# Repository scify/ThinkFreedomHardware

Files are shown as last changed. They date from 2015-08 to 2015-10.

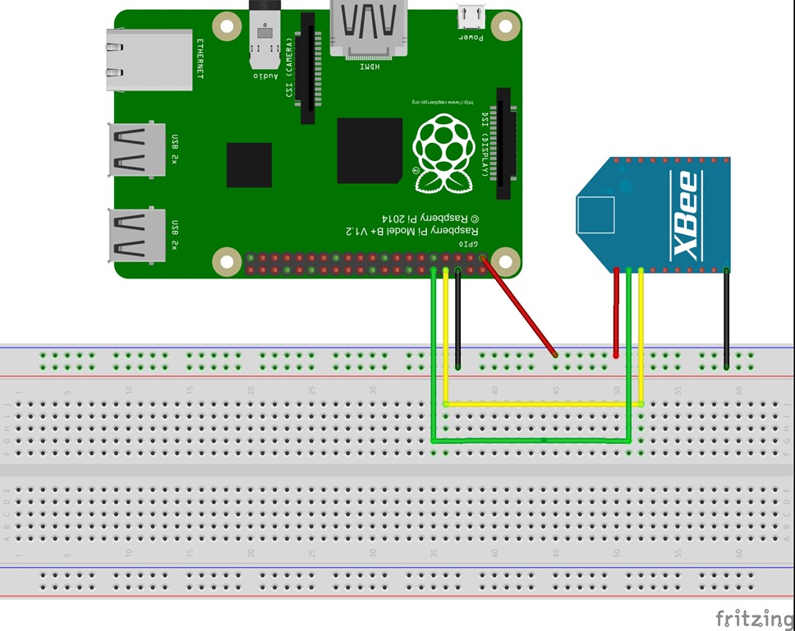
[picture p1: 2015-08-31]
Stuff/Pictures-Schematics/xbee on pi shematic.jpg

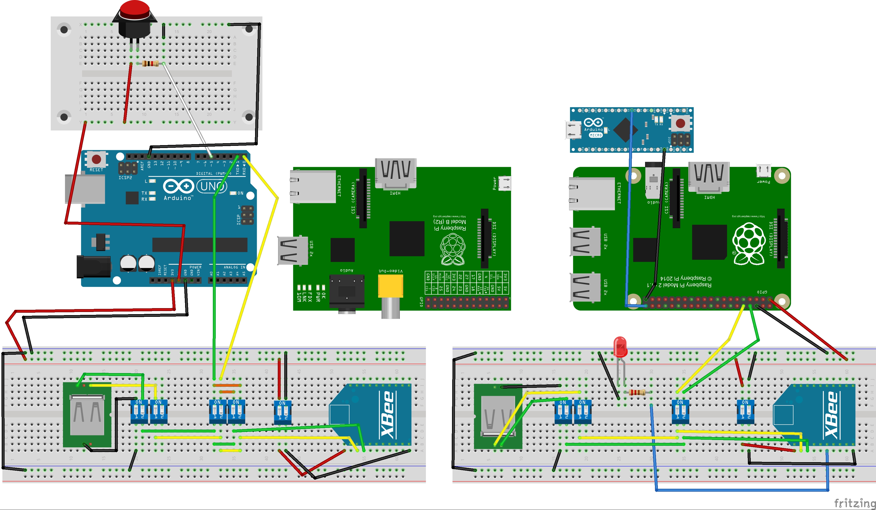
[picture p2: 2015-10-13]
Scematics(Fritzing)/ThinkFreedomStack Schematic(Fritzing)_bb.jpg

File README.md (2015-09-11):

# ThinkFreedom Hardware Stack

The ThinkFreedom Hardware Stack is a hardware stack definition aimed to provide
an open implementation architecture under a
*sensor-stimulus-reactor* paradigm, supporting different settings of the
Internet of Things (IoT).

This specific project refers to the first draft of the hardware stack
definition and a first implementation, as a
device which is especially designed for disabled people. The goal of this
project is to help this group of people to interact with devices in their home
and use the PC and to better communicate with other people.

In this repository you will find a hardware prototype that was built during an
internship at SciFY (www.scify.org). This project is an openhardware-opensource
project.

## Box
Contains 2 versions (v1 and v2) of a 3D design model of the controller . You
can open them with the open source FreeCad program. It contains also a folder
with failed attempts and some examples.

## Code
Contains 3 code "packages".

1. ControlUnitPython.py  this python script runs on the Raspberrry Pi 2
2. TFS_Leonardo.ino this arduino script runs on the Arduino Leonardo/Micro
located in the control unit .
3. TFS_input.ino this arduino script runs on the Arduino Uno located in the
controller

Both arduino scripts can be edited and uploaded with the Arduino program. For
more information on how to use the code snippets check the "Manual of
Prototype" document.

## Schematics(Fritzing)
Contains 2 files.

1. ThinkFreedom Stack.jpg  this is a simple image of the schematic of the
prototype
2. TFS_Leonardo.ino this is a fritzing file which can be edited by the Fritzing
program : http://fritzing.org/home/

## Stuff

Contains several things that helped as along the way.

1. Pictures-Schematics: this file has several schematics images that we
considered when we were making the prototype
2. Alternate Input Ways.docx:  this doc has helpful descriptions of assistive
technology products
3. Switches for Think Freedom.xlsx this ecxel file is one of our first research
of switches that could be used for our application.

## ThinkFreedomStack Specs

Contains the specs for the project as well as it contains the architecture (
1.Layers of TFS(OSI Model).xlsx ) we used to build the prototype. The last file
has 3 additional implementations of the hardware stack and approximations of
costs.

## Manual For Prototype
A step by step guide of how you are going to build the prototype that we
developed.

## TFS_Presentation
Is a presentation of our work on Prezi.

## License

[](http://
creativecommons.org/licenses/by/4.0/)
ThinkFreedom Hardware by [SciFY](http://www.scify.org) is licensed under
a [Creative Commons Attribution 4.0 International
License](http://creativecommons.org/licenses/by/4.0/).
Based on a work at
[https://github.com/scify/ThinkFreedomHardware](https://github.com/scify/
ThinkFreedomHardware).

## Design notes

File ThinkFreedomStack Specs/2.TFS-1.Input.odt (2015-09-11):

TFS 1. Input

The input in general should changeable, it depends on the person that is going to use the device . For different type of inputs it should give the same signal to the control unit(for example the input can be buttons ,a joystick , a camera or it can be sensors). Keeping that in mind for selecting the input. It can be:

Buttons/Switches:

-It can be a Button. This requires the help from the software. For example a keyboard, there has to be a way of moving from key to key and the button should be the selection.

-It can be a combination of Buttons. This way more complex things can be operated by the user. The help from for the software is much less needed.

There are a lot types of buttons/switches that can be used. Link:

https://docs.google.com/spreadsheets/d/1ZvIIkGd06QHr9OYzwCT2-BUQOSj6Ud6AHfjPr6JeUGU/edit?usp=sharing

Sensors:

The type of sensors that can be used are:

-Optical. It can be a camera that can detect movement. It can be eye movement, face gestures, head movement or body movement.

-Tilt. The user can just move his head to operate the system.

An interesting idea is this : https://www.youtube.com/watch?v=ikD_3Vemkf0

Joystick:

Instead of a mouse(or something else with the help of the software) the user will use a joystick. It can be combined with buttons for clicking or selecting.

Some other input ways can be found here:

https://docs.google.com/document/d/1bNMofBS1oewYr8HfNjX6Wp-dU_9WeOqa6330RUK6RvI/edit?usp=sharing

Specs about the way the signal is going through the channel.

The trigger from the input must be altered so it can much the channel that is going to be transmitted to the control unit. That means it must support the way the control unit receives the signals ( for example via bluetooth, cable, internet).

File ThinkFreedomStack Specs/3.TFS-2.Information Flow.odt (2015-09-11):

TFS-2.Information Flow

Αυτό το επίπεδο περιλαμβάνει τη μεταφορά της πληροφορίας του φυσικού ερεθίσματος στην μονάδα επεξεργασίας στην σωστή μορφή . Αναλύοντας αυτό το επίπεδο ξεχωρίζουμε χονδρικά : κωδικοποίηση της ερεθίσματος , μεταφορά του μέσω καναλιού , αποκωδικοποίηση και εισαγωγή του στην μονάδα επεξεργασίας .

Οι πιο πρακτικοί τρόποι υλοποίησης αυτού το επίπεδου για αυτό το project είναι με καλώδιο (USB) , ZigBee, bluetooth , υπέρυθρες και ίσως Wi-fi ή GSM .

Για τα παραπάνω υπάρχουν πολλές διαφορετικές επιλογές στο εμπόριο όπως :

http://gr.mouser.com/Embedded-Solutions/RF-Wireless-Modules/Bluetooth-802151-Modules/_/N-6l7pgZscv7Zlls6

https://www.microchip.com/pagehandler/en-us/technology/bluetooth/home.html

http://www.zigbee.org/

...για περισσότερα Wi-fi ανατρέξτε στο αρχείο Layer 2-Inputs and Outputs σελίδα 7

Όμως, επειδή για τέτοιες εφαρμογές υπάρχει πολύ υλικό και υποστήριξη στο internet χρησιμοποιώντας το arduino και το raspberry pi κτλ , είναι μια πολύ καλή και φτηνή λύση με μεγάλη συμβατότητα στους διαφορετικούς τρόπους σύζευξης συσκευών με αυτά .

Άρα ,

Κωδικοποίηση ερεθίσματος

-Κάποιο arduino μικρής κατανάλωσης και μεγέθους .

https://www.arduino.cc/en/Main/Products

-Intel Edison (μικρή κατανάλωση και μέγεθος , συμβατότητά , Linux , )

http://download.intel.com/support/edison/sb/edison_pb_331179001.pdf

-Intel Galileo (συμβατό με Αrduino Uno Shields , ethernet )

http://www.intel.com/newsroom/kits/quark/galileo/pdfs/Intel_Galileo_Datasheet.pdf

Μεταφορά μέσω καναλιού + αποκωδικοποίηση και εισαγωγή του στην μονάδα επεξεργασίας

(USB)

-Απλή σύνδεση του arduino με μακρύ καλώδιο USB (ή micro-USB) και στις δυο άκρες

(Bluetooth)

- Χρήση κατάλληλου bluetooth chip για το οποίο υπάρχουν έτοιμες βιβλιοθήκες για arduino

http://www.ebay.com/bhp/arduino-bluetooth

https://store.arduino.cc/index.php?main_page=advanced_search_result&search_in_description=1&keyword=bluetooth&btnG=search

(Υπέρυθρες)

-Αντίστοιχο με το προηγούμενο

http://www.ebay.com/bhp/arduino-ir-sensor

(Wifi)

-Ένα Wi-fi Shield μπορεί να παρέχει μη τοπική επεξεργασία της πληροφορίας με δυνατότητα επικοινωνίας με από σημεία στο χώρο με wifi

http://www.ebay.com/sch/i.html?_from=R40&_trksid=p2053587.m570.l1313.TR0.TRC0.H0.Xwifi+shield+arduino.TRS0&_nkw=wifi+shield+arduino&_sacat=0

(GSM)

-Αντίστοιχο με το προηγούμενο μόνο που εδώ έχουμε επικοινωνία (σχεδόν) σε κάθε χωρικό σημείο

https://www.arduino.cc/en/Main/ArduinoGSMShield

http://www.ebay.com/sch/i.html?_odkw=wifi+shield+arduino&_osacat=0&_from=R40&_trksid=p2045573.m570.l1313.TR0.TRC0.H0.XGSM+shield+arduino.TRS0&_nkw=GSM+shield+arduino&_sacat=0

Τώρα , μπορεί να γίνει και συνδυασμός των παραπάνω για μια πιο ολοκληρωμένη λύση . Για παράδειγμα , όταν υπάρχει ταυτόχρονα bluetooth και wifi (ή GSM) και η σύνδεση μέσω του πρώτου διακοπεί ,τότε μπορεί να αναλάβει το δεύτερο ενεργοποιώντας διαφορετικές δυνατότητες του λογισμικού . Πιο συγκεκριμένα , επειδή η διακοπή της σύνδεσής με bluetooth σημαίνει οτι , είτε ότι το άτομο απομακρύνθηκε από το χώρο , είτε μια διακοπή του ρεύματος , είτε γενικότερη αποτυχία στην σύνδεση , τότε το wifi και το GSM θα παρέχει μια μεγαλύτερή κάλυψη ώστε σε περίπτωση ανάγκης να αποστέλνεται ένα email ή sms.

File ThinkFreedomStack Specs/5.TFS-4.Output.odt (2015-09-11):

TFS-4.Output

In general we want the output device to be pretty much everything (TV, smart TV, PC, tablet). After the Control Unit we want the signal to be sent to an adaptor. The adaptor will alter the signal so it will match the output devices in each case.

The communication between the Control Unit and the adaptor it’s going to be materialized in many ways so the Think Freedom device is going to be more easy to use and more accessible for everyone. The communication ways are via Internet(wifi and ethernet), cable, bluetooth.

TV

If the Think Freedom device is going to be connected to a TV(via VGA or HDMI) the Control Unit should be able to support an OS or a specific software.

Smart TV

Here the software can be installed in the smart TV so the Control Unit should only give the signal to trigger some functions in the software. Also the Smart TV can be connected to internet, for distant control.

PC

If the output device is a PC the Think Freedom device should work like an input device for the PC, like a mouse or a keyboard. The laptop must have the software of Think Freedom installed.

Tablet

For the Think Freedom device to work on a tablet there has to be an app for the tablet. The device can be connected via bluetooth or internet with the tablet.

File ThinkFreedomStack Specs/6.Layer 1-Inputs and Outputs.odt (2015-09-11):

Layer 1-Inputs and Outputs

Inputs

-Buttons/switch

This type of input is a signal(pulse). Τhe signal can be 1V-5V.

This applies to the buttons/switches with a mono phone plug output. The tip send the signal and the sleeve is the ground. The circuit is shown below:

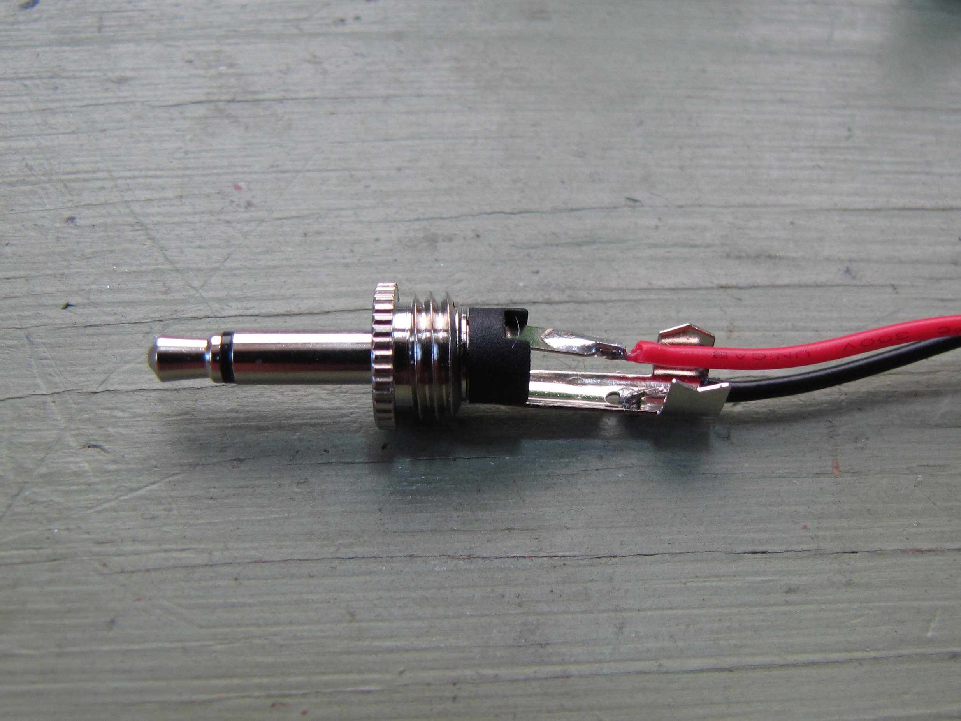
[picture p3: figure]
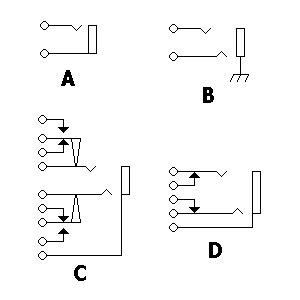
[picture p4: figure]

Left the mono phone plug. Right the A the input.

- joystick

The types of joysticks a many. The most common one is the type that works like a combination of buttons.

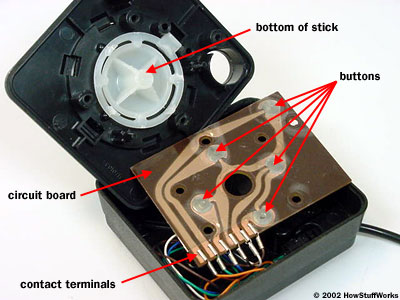
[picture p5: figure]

The button type switch circuit

The output of this is either a usb device or some kind of connector.

-Camera

If a camera is going to be the input, we need some process in this level. Also we need the help of the software in a next level. Also that means that the input layer must have a driver to support a camera.

-Sensors

The type of signal we are going to have depends on the sensor we are going to use. In general is pretty easy to handle the signal of a sensor with a microcontroller.

The signal from from the sensor depends on the type of sensor we are going to use. In general it is from some mVs to some Volts. This signal must be processed

Some sensors are:

pressure sensor

A pressure sensor is generally a variable resistor that changes resistance based on how hard it is pressed. They are also known as Force Sensing Resistors or FSRs. They come in many shapes and sizes, from tiny little dots to long strips. They're pretty flexible, and can usually be cut to size.

Often you use an FSR as the variable resistor in a voltage divider circuit. By using one FSR and one fixed resistor and hooking Vout to an A/D converter you can give the microcontroller some idea of how much pressure is being put on the FSR. If you don't have an A/D converter handy, there's a simple RCtime circuit that you can use to do more-or-less the same thing.

FSRs can be used in many places that a button is used, with the advantage that you can not only tell that the button is being pressed, but also how hard. They're used a lot in things like velocity-sensitive keyboards, but are also good for use in floor mats, on the sides of instruments, on finger tips...Basically anywhere there's going to be a force that you want to measure.

light sensor

The most common light sensor is the CDC photo sensor. It works like a variable resistor with a value that changes based on how much light it receives. Other types are photo-transistors and photo-diodes.

Photo sensors are used in much the same way as pressure sensors. If you hook one up to a microcontroller via a voltage divider (or RCtime) circuit, the microcontroller can sense how much light is falling on the device.

beam breaker

A beam breaker is a non-physical switch or trigger. The simplest way to make one is to aim a cheap laser pointer at a photo-sensor. When the beam is broken, the resistance of the photo-resistor changes. If the photo resistor is hooked up to a microcontroller, it can sense whether the beam is intact or broken. So simple!

proximity sensor

There are a variety of ways to implement proximity sensing. The most common are infrared and ultrasound. They're both usually used as packaged devices that hook up to a microcontroller via one or more digital i/o lines.

An infrared sensor works by sending out pulses of infrared (invisible) light. It then tries to detect reflections of that light from nearby objects. If it detects a reflection then it assumes that there's an object nearby and puts out a digital "1". Otherwise it puts out a "0". There are some tricks to get a rough distance measurement out of an infrared detector, but most often they're used for simple object detection.

An ultrasonic proximity detector works by putting out ultrasonic (inaudible) pulses of sound. It then measures the length of time it takes those pulses to hit nearby objects and return as echos. The longer the time, the farther away the object. Ultrasonic proximity detectors are good for measuring short distances (maybe a couple yards). It's usually up to the microcontroller to do the counting and distance computations; the detector takes care of sending and detecting the ultrasonic pulses.

accelerometer

Accelerometers are cool. They're small ICs with tiny little suspended weights embedded in them. By measuring the force of gravity/inertia on those weights the device can emit a digital signal that tells you about its orientation in space.

Like proximity sensors, accelerometers are hooked up to a microcontroller via a few digital i/o lines.

microphone

Most microcontrollers aren't fast enough to be useful for recording sound via a mic. But they can do some basic things like listen for suddens sounds or listen for silence. They can also be used to control sound recording devices.

contact mic

These are made from piezo elements. A piezo element is made from a curious type of ceramic material that gives off electricity when it's deformed (this is called the piezo-electric effect). The voltage created is (roughly) proportional to how much the element is deformed. This property lets it be used as a contact mic. You can scream all you want into a contact mic and it won't hear you. But rub it against something, and it will wail! There are other types of piezo materials, like piezo rubber.

Output

-cable

usb 2.0

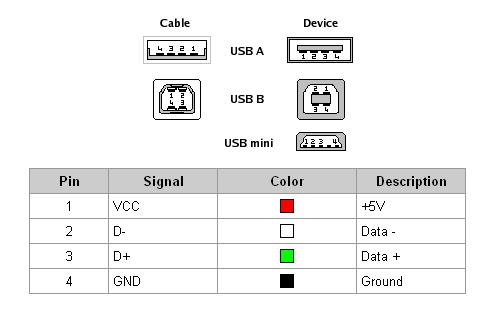
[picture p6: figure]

As we can see there are four pins for the usb . Two pins VCC 5v,Ground and two pins for the data (D+,D-).

Max signaling rate 480Mbit/s.

usb 3.0

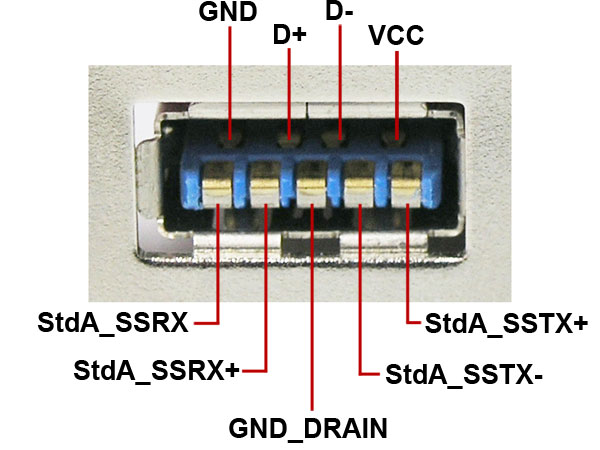
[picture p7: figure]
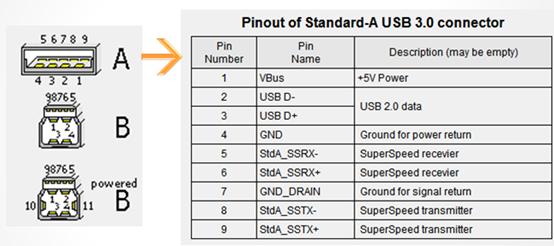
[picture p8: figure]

Throughput 4Gbits/sec.

In conclusion using a usb cable we need a signal in (pulse) and 5V power supply.

-Bluetooth

Bluetooth is a wireless technology standard for exchanging data over short distances (using short-wavelength UHF radio waves in the ISM band from 2.4 to 2.485 GHz] (https://en.wikipedia.org/wiki/Bluetooth#cite_note-4)) from fixed and mobile devices, and building personal area networks (PANs).

Bluetooth operates at frequencies between 2400 and 2483.5 MHz (including guard bands of 2 MHz at the bottom end and 3.5 MHz at the top).This is in the globally unlicensed (but not unregulated) Industrial, Scientific and Medical (ISM) 2.4 GHz short-range radio frequency band. Bluetooth uses a radio technology called frequency-hopping spread spectrum. Bluetooth divides transmitted data into packets, and transmits each packet on one of 79 designated Bluetooth channels. Each channel has a bandwidth of 1 MHz. Bluetooth 4.0 uses 2 MHz spacing, which accommodates 40 channels. The first channel starts at 2402 MHz and continues up to 2480 MHz in 1 MHz steps. It usually performs 1600 hops per second, with Adaptive Frequency-Hopping (AFH) enabled.

Originally, Gaussian frequency-shift keying (GFSK) modulation was the only modulation scheme available. Since the introduction of Bluetooth 2.0+EDR, π/4-DQPSK (Differential Quadrature Phase Shift Keying) and 8DPSK modulation may also be used between compatible devices. Devices functioning with GFSK are said to be operating in basic rate (BR) mode where an instantaneous data rate of 1 Mbit/s is possible. The term Enhanced Data Rate (EDR) is used to describe π/4-DPSK and 8DPSK schemes, each giving 2 and 3 Mbit/s respectively. The combination of these (BR and EDR) modes in Bluetooth radio technology is classified as a "BR/EDR radio".

Bluetooth is a packet-based protocol with a master-slave structure. One master may communicate with up to seven slaves in a piconet. All devices share the master's clock. Packet exchange is based on the basic clock, defined by the master, which ticks at 312.5 µs intervals. Two clock ticks make up a slot of 625 µs, and two slots make up a slot pair of 1250 µs. In the simple case of single-slot packets the master transmits in even slots and receives in odd slots. The slave, conversely, receives in even slots and transmits in odd slots. Packets may be 1, 3 or 5 slots long, but in all cases the master's transmission begins in even slots and the slave's in odd slots.

The above is valid for "classic" BT. Bluetooth Low Energy, introduced in the 4.0 specification, uses the same spectrum but somewhat differently

Officially Class 3 radios have a range of up to 1 metre (3 ft), Class 2, most commonly found in mobile devices, 10 metres (33 ft), and Class 1, primarily for industrial use cases,100 metres (300 ft). Bluetooth Marketing qualifies that Class 1 range is in most cases 20–30 metres (66–98 ft), and Class 2 range 5–10 metres (16–33 ft).

Table of power and range per class

Class | Max permitted power (mW) | Max permitted power (dB) | Range (m)
1 | 100 | 20 | 100
2 | 2.5 | 4 | 10
3 | 1 | 0 | 1

Table of data rate and throughput per Version

Version | Data rate | Max application throughput
1.2 | 1 Mbit/s | >80 kbit/s
2.0+EDR | 3 Mbit/s | >80 kbit/s
3.0+HS | 24 Mbit/s | See (https://en.wikipedia.org/wiki/Bluetooth#Bluetooth_v3.0_.2B_HS)Version 3.0 + HS (https://en.wikipedia.org/wiki/Bluetooth#Bluetooth_v3.0_.2B_HS)
4.0 | 24 Mbit/s | See (https://en.wikipedia.org/wiki/Bluetooth#Bluetooth_v4.0)Version 4.0 LE (https://en.wikipedia.org/wiki/Bluetooth#Bluetooth_v4.0)

- ZigBee

ZigBee is poised to become the global control/sensor network standard. It has been designed to provide the following features:

- Low power consumption, simply implemented
  - Users expect batteries to last many months to years! Consider that a typical single family house has about 6 smoke/CO detectors. If the batteries for each one only lasted six months, the home owner would be replacing batteries every month!
- In contrast to Bluetooth, which has many different modes and states depending upon your latency and power requirements, ZigBee/IEEE 802.15.4 has two major states: active (transmit/receive) or sleep. The application software needs to focus on the application, not on which power mode is optimum for each aspect of operation.
- Even mains powered equipment needs to be conscious of energy. ZigBee devices will be more ecological than their predecessors saving megawatts at it full deployment. Consider a future home that has 100 wireless control/sensor devices,
  - Case 1: 802.11 Rx power is 667 mW (always on)@ 100 devices/home & 50,000 homes/city = 3.33 megawatts
  - Case 2: 802.15.4 Rx power is 30 mW (always on)@ 100 devices/home & 50,000 homes/city = 150 kilowatts
  - Case 3: 802.15.4 power cycled at .1% (typical duty cycle) = 150 watts
- Low cost to the users means low device cost, low installation cost and low maintenance.
  - ZigBee devices allow batteries to last up to years using primary cells (low cost) without any chargers (low cost and easy installation). ZigBee's simplicity allows for inherent configuration and redundancy of network devices provides low maintenance.
- High density of nodes per network
  - ZigBee's use of the IEEE 802.15.4 PHY and MAC allows networks to handle any number of devices. This attribute is critical for massive sensor arrays and control networks.
- Simple protocol, global implementation
  - ZigBee's protocol code stack is estimated to be about 1/4th of Bluetooth's or 802.11's. Simplicity is essential to cost, interoperability, and maintenance. The IEEE 802.15.4 PHY adopted by ZigBee has been designed for the 868 MHz band in Europe, the 915 MHz band in N America, Australia, etc; and the 2.4 GHz band is now recognized to be a global band accepted in almost all countries.

ZigBee/IEEE 802.15.4 - General Characteristics

- Dual PHY (2.4GHz and 868/915 MHz)
  - Data rates of 250 kbps (@2.4 GHz), 40 kbps (@ 915 MHz), and 20 kbps (@868 MHz)
  - Optimized for low duty-cycle applications (<0.1%)
  - CSMA-CA channel access
  - - Yields high throughput and low latency for low duty cycle devices like sensors and controls
  - Low power (battery life multi-month to years)
  - Multiple topologies: star, peer-to-peer, mesh
  - Addressing space of up to:
  - - 18,450,000,000,000,000,000 devices (64 bit IEEE address)
  - - 65,535 networks
  - Optional guaranteed time slot for applications requiring low latency
  - Fully hand-shaked protocol for transfer reliability
  - Range: 50m typical (5-500m based on environment)

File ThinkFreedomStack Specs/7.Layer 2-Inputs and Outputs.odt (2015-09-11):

Layer 2 - Inputs and Outputs

Περιγραφή Απαιτήσεων

*Τα κείμενα σε γκρι χρώμα είναι επιβοηθητικά.

Η επικοινωνία ανάμεσα στη μονάδα επεξεργασίας και και το σύστημα που υλοποιεί το ερέθισμα θα πρέπει να έχουν αμερόληπτη επικοινωνία μεταξύ τους . Παρόλα αυτά οι απαιτήσεις του έργου δεν είναι υψηλές και επομένως μπορούν να προσδιοριστούν κάποιες απλές προδιαγραφές :

Για ενσύρματη επικοινωνία

Θα πρέπει να επιτυγχάνεται μια μετάδοση παλμός σε ακολουθία , η οποία θα διαμορφώνεται από το προηγούμενο layer στου οποίου θα είναι η έξοδος

Δεν έχουμε απαίτηση μεγάλου μήκους καλωδίου , οπότε δεν μας απασχολεί η ποιότητα του καλωδίου διότι η εξασθένηση και η διασπορά των παλμών θα είναι αμελητέες.

Η τάση λειτουργίας είναι ένα από τα μελήματα μας καθώς σε dc δεν πρέπει να ξεπερνιούνται τα 100 V . Η εφαρμογή μας όμως είναι τέτοιας κλίμακας που δεν μας απασχολεί κάτι τέτοιο .

Ενδεικτικά το άνω όριο της ίασης που θα χρησιμοποιήσουμε είναι στα 5V .

Ας έχουμε στο μυαλό μας πως το καλώδιο θα πρέπει να είναι καλά ενισχυμένο και μονωμένο . Οι ασθενείς που θα το χρησιμοποιήσουν δεν είναι σε θέση να πραγματοποιήσουν ακριβής κινήσεις ώστε να προσέξουν τις προκαλούμενες καταπονήσεις που μπορεί να προκαλέσουν στο καλώδιο . Αντοχή στον εφελκυσμό , αντοχή στον τεμαχισμό, αντοχή στις υψηλές θερμοκρασίες , υψηλή μόνωση πρέπει να εξασφαλιστούν ώστε να μην διακοπεί πότε η επικοινωνία .

Φυσικά και οι δυο άκρες πρέπει να μιλούν την ίδια `γλώσσα` . Αυτό σημαίνει πως πρέπει να υπάρχει ένα ενιαίο πρωτόκολλο επικοινωνίας . Αυτό θα πρέπει να καθορίζει το τι θα στέλνει η συσκευή ώστε ο παραλήπτης , η μονάδα επεξεργασίας , να το καταλαβαίνει . Δηλαδή και οι δυο άκρες πρέπει να μετασχηματίζουν το μήνυμα σύμφωνα με ένα κανόνα που θα έχουν από κοινού , ακόμα και αν τρέχουν διαφορετικά λειτουργικά συστήματα . Υπάρχουν ήδη πολλές αναπτυσσόμενες τεχνολογίες που προσφέρουν μεγάλη συμβατότητα και εμείς θα επιλέξουμε μια ευρέος διαδεδομένη .

Για ασύρματη επικοινωνία

Πάλι εδώ πρέπει να αποστείλουμε ένα μήνυμα αποτελούμενο από μια ακολουθία παλμών (ψηφιακή μετάδοση ) αλλά αυτήν την φορά ασύρματα , δηλαδή ακολουθία ηλεκτρομαγνητικών παλμών οι οποίοι παράγονται από την έξοδο του προηγουμένου από αυτού layer .

(

Considerations in choosing a carrier frequency

Carrier frequency

Signal that is modulated to carry data

Frequency is not equal to bandwidth

Ability to carry data (modulation rate)

Availability of devices to transmit and receive signals

Interference from other devices in same band *

ISM bands limit power output

Interactions of radiation with environment absorption by water, metal, building materials, foliage

Reflection and multi-path properties constructive/destructive interference patterns (e.g., nulls)

)

Ο ρυθμός μετάδοσης των bit δεν έχει πολύ σημασία αφού τεχνολογίες υπερκαλύπτουν της απαιτήσεις του έργου

Δεν έχουμε απαίτηση μεγάλης απόστασης μετάδοσης αφού η ασύρματη σύνδεση που θέλουμε να πραγματοποιήσουμε είναι σε μικρή απόσταση ( ~ 10m ) και επιθυμούμε μια απλή και άμεση επικοινωνία δυο συσκευών . Επομένως δεν χρειάζεται να στηθεί κάποιο κεντρικό σημείο πρόσβασης . Αντιπροσωπευτικός τύπος μιας τέτοιες σύνδεσης είναι το ad hoc (point-to-point) τύπος δικτύου (βλ. Bluetooth κτλ) . Προσφέροντας έτσι ευελιξία , ελάχιστη διαμόρφωση , γρήγορη εγκατάσταση (και αλλά) στον τρόπο σύνδεσης ανάμεσα στις συσκευές , αυτό δεν σημαίνει παράλληλα πως ένα access point (Star pattern) δίκτυο δεν είναι κατάλληλο (βλ Wifi , Cellular κτλ ) .

Μας απασχολεί το εύρος συχνοτήτων που θα καταλαμβάνει ώστε να μην έχουμε παρεμβολές . Οι διαθέσιμες συχνότητες για την εφαρμογή μας είναι από τα 300 MHz έως τα 30 GHz περίπου . Μερικές από αυτές τις συχνότητες μέσα σε αυτό το εύρος είναι αξιοποιήσιμες για την εφαρμογή μας , διότι πολλές είναι , και πάλι , δεσμευμένες για άλλες χρήσεις . Ως γνωστόν διαφορετικές συχνότητες προσδίδουν διαφορετικά χαρακτηριστικά ανάκλασης , διάθλασης , περίθλασης άλλα εδώ δεν μας απασχολούν πολύ αυτά γιατί δεν έχουμε μεγάλες αποστάσεις ούτε και σημαντικά εμπόδια .Επίσης προτείνεται η διαίρεση στο χρόνο πολύπλεξη (TDM) για την αμφίδρομη επικοινωνία διότι είναι πιο αξιόπιστη. Σε περιπτώσεις που το εύρος που επιλέγει υπερκαλύπτει μερικώς ή τελείως υπηρεσίες με αντίστοιχα εύρη , τότε να ληφθούν υπόψη οι τεχνικές FDSS και DSSS.

Προτεινόμενες τεχνολογίες είναι Bluetooth (2,4-2,485GHz) , WiFi/802.11b/g and Bluetooth: 2.4GHz , Cell phones: 824-849MHz, 869-894MHz, 1850-1990MHz , Zigbee/802.15.4: 868MHz, 915MHz, 2.4GHz .

Η κατανάλωση ισχύος πρέπει να είναι μικρή γιατί η συχνή φόρτιση του ασύρματου χειριστηρίου θα δυσχεραίνει την επικοινωνία με την μονάδα επεξεργασίας . Για τον ασθενή δεν είναι αυτονόητο πως θα μπορεί εύκολα να φορτίζει το χειριστήριο συχνά και επίσης δεν πρέπει να κοπεί ξαφνικά η σύνδεση . Άρα , η τεχνολογία που θα επιλέγει πρέπει να είναι χαμηλής κατανάλωσης (βλ. ZigBee , Bluetooth κτλ )

Προς την ίδια κατεύθυνση πρέπει και το πρωτόκολλο επικοινωνίας να επιτρέπει την εύκολη διακοπή της σύνδεσης . Ακόμα και αν η τεχνολογία , που τελικά θα επιλέγει , καθορίσει τα διαθέσιμα πρωτόκολλα που μπορούμε να επιλέξουμε , αυτό δεν σημαίνει πως δεν χρειάζεται να ασχοληθούμε με αυτά . Αν κάποιος διαλέξει να υλοποιήσει μια διαφορετική τεχνολογία , το πρωτόκολλο επικοινωνίας πρέπει να εξασφαλίζει την επιτυχία παράδοσης του μηνύματος στον παραλήπτη με κάθε κόστος και ίσως να εκφράζει ένα ασύρματο προσωπικό δίκτυο (WPAN)

ZigBee καλό http://courses.cs.washington.edu/courses/csep567/10wi/lectures/Lecture8.pdf

(

Radio Protocols for Wireless Networks

UHF (300-1000MHz)

Mote radio

WiFi (2.4GHz)

Wireless LAN Bluetooth (2.4GHz)

Common in many consumer devices (PDAs, cell phones, etc.)

Zigbee (850-930MHz)

Next generation radio for sensor networks and consumer devices

Bluetooth

Short-range radio at 2.4GHz

Available globally for unlicensed users

Low-power Low-cost Cable replacement

Devices within 10m can share up to 1Mb/sec – 700Kb/sec effective

Universal short-range wireless capability

Bluetooth Application Areas

Data and voice access points

Real-time voice and data transmissions

Cordless headsets

Three-in-one phones: cell, cordless, walkie-talkie

Cable replacement

Eliminates need for numerous cable attachments for connection

Automatic synchronization when devices within range

Ad hoc networking

Can establish connections between devices in range

Devices can “imprint” on each other so that authentication is not required for each instance of communication

Support for object exchange (files, calendar entries, business cards)

)

[synexeia apo https://el.wikipedia.org/wiki/%CE%91%CF%83%CF%8D%CF%81%CE%BC%CE%B1%CF%84%CE%BF_%CE%B4%CE%AF%CE%BA%CF%84%CF%85%CE%BF

https://en.wikipedia.org/wiki/Wireless#Wireless_services

https://en.wikipedia.org/wiki/Bluetooth]

Εύρεση υπαρχόντων λύσεων

Σε αυτό το σημείο θα γίνει η αντιστοίχηση των παραπάνω προδιαγραφών κάποιες τεχνολογίες που τις πληρούν σε πολύ καλό βαθμό.

Για ενσύρματη επικοινωνία

USB

Το USB σχεδιαστικέ για να βοηθήσει την σύνδεση διαφόρων συσκευών με τον υπολογιστή με έναν κοινό τρόπο . Επομένως ικανοποιεί πολύ καλά τις προδιαγραφές μας και είναι μια δομημένη και προτιμητέα σύνδεση από πολλές εφαρμογές.

Υπάρχει αναφορά στην περιγραφή του Layer 1.

Δεν χρειάζεται να μπούμε σε λεπτομέρειες υλοποίησης για το συγκεκριμένο έργο γιατί οι περισσότερες ενσύρματες διεπαφές προβλέπουν ένα USB.

Για ασύρματη επικοινωνία

ZigBee

Ας έχουμε υπόψη ότι τόσο το πρότυπο Bluetooth όσο και το ZigBee θεωρούνται ως μια ασύρματη USB σύνδεση.

Ο όρος Zigbee αναφέρεται στο πρότυπο ΙΕΕΕ 802.15.4 το οποίο περιγράφει μια ομάδα πρωτοκόλλων για την επικοινωνία ραδιοσυκευών πολύ μικρού μεγέθους, κόστους και πολύ χαμηλής ισχύος. Το πρότυπο στοχεύει στα ασύρματα προσωπικά δίκτυα και συγκεκριμένα στοχεύει στην αντικατάσταση του Bluetooth καθώς οι ραδιοσυσκευές του πρότυπου Zigbee είναι πιο φτηνές και απαιτούν περίπου το 50% του κώδικα που χρειάζεται μια συσκευή Bluetooth για τον έλεγχο τους (κατά συνέπεια απαιτούν λιγότερο χώρο στη μνήμη της φορητής συσκευής – γεγονός σημαντικό για τις μικρές μνήμες). Το πρότυπο χρησιμοποιεί τις ίδιες συχνότητες με το Bluetooth μπορεί να χρησιμοποιηθεί για ασύρματη επικοινωνία χαμηλών ταχυτήτων όπου η ασφάλεια και η διάρκεια ζωής της μπαταρίας είναι τα βασικά στοιχεία.

Παρατίθενται κάποια βασικά χαρακτηριστικά του που το δικαιολογούν ως μια ικανοποιητική λύση για το έργο.

-Simple protocol (small memory footprint for protocol stack)

-Broadcast support (unlike Bluetooth)

-Full network support (up to 64-bit addresses)

-Very low power (batteries that last years)

-Consumer device networks

-Remote monitoring and control

-Low-cost, low-complexity

-Support ad-hoc and mesh networking

-Industry consortium

-Builds on IEEE standard 802.15.4 physical radio standard – OQSK encoding (offset quadrature phase shift keyed)

-Adds logical network, security and application software 250Kb/sec bandwidth – 128Kb/sec effective, 30m range at 2.4GHz 40Kb/sec at 915MHz

Υπάρχει αναφορά στην περιγραφή του Layer 1.

Τα ακριβής χαρακτηριστικά μερικών μοντέλων βρίσκονται παρακάτω :

https://www.silabs.com/products/wireless/zigbee/Pages/zigbee-chips.aspx

http://www.digi.com/products/wireless-wired-embedded-solutions/zigbee-rf-modules/zigbee-mesh-module/xbee-zigbee#overview

http://www.zigbee.org/zigbee-products-2/#zigbeecertifiedproducts/?view_30_filters=%5B%7B%22field%22%3A%22field_3%22%2C%22operator%22%3A%22is%22%2C%22value%22%3A%22551ed892f6cde90637f85dcb%22%7D%5D&view_30_page=1

Bluetooth

Το Bluetooth είναι ένα βιομηχανικό πρότυπο για ασύρματα προσωπικά δίκτυα υπολογιστών (Wireless Personal Αrea Νetworks, WPAN (https://el.wikipedia.org/wiki/WPAN)). Πρόκειται για μια ασύρματη τηλεπικοινωνιακή (https://el.wikipedia.org/wiki/%CE%A4%CE%B7%CE%BB%CE%B5%CF%80%CE%B9%CE%BA%CE%BF%CE%B9%CE%BD%CF%89%CE%BD%CE%AF%CE%B5%CF%82) τεχνολογία μικρών αποστάσεων, η οποία μπορεί να μεταδώσει σήματα (https://el.wikipedia.org/wiki/%CE%A3%CE%AE%CE%BC%CE%B1_(%CE%B7%CE%BB%CE%B5%CE%BA%CF%84%CF%81%CE%BF%CE%BB%CE%BF%CE%B3%CE%AF%CE%B1)) μέσω μικροκυμάτων (https://el.wikipedia.org/wiki/%CE%9C%CE%B9%CE%BA%CF%81%CE%BF%CE%BA%CF%8D%CE%BC%CE%B1%CF%84%CE%B1) σε ψηφιακές (https://el.wikipedia.org/w/index.php?action=edit&redlink=1) συσκευέ (https://el.wikipedia.org/w/index.php?title=%CE%A3%CF%85%CF%83%CE%BA%CE%B5%CF%85%CE%AE&action=edit&redlink=1)ς .Ας έχουμε υπόψη ότι τόσο το πρότυπο Bluetooth όσο και το ZigBee θεωρούνται ως μια ασύρματη USB σύνδεση. Παρατίθενται κάποια βασικά χαρακτηριστικά του που το δικαιολογούν ως μια ικανοποιητική λύση για το έργο.

Protocol Architecture

Cable replacement protocol

RFCOMM

Telephony control protocol

Telephony control specification – binary (TCS BIN)

Adopted protocols

PPP

TCP/UDP/IP

OBEX

WAP

Profiles – vertical slide through the protocol stack

Basis of interoperability

Each device supports at least one profile

Defined based on usage models e.g., headset, camera, personal server, etc.

Bluetooth

Short-range radio at 2.4GHz

Available globally for unlicensed users

Low-power Low-cost Cable replacement

Devices within 10m can share up to 1Mb/sec – 700Kb/sec effective

Universal short-range wireless capability

Bluetooth Application Areas

Data and voice access points

Real-time voice and data transmissions

Cordless headsets

Three-in-one phones: cell, cordless, walkie-talkie

Cable replacement

Eliminates need for numerous cable attachments for connection

Automatic synchronization when devices within range

Ad hoc networking

Can establish connections between devices in range

Devices can “imprint” on each other so that authentication is not required for each instance of communication

Support for object exchange (files, calendar entries, business cards)

Υπάρχει αναφορά στην περιγραφή του Layer 1.

Τα ακριβής χαρακτηριστικά μερικών μοντέλων βρίσκονται παρακάτω :

http://www.ebay.com/bhp/arduino-bluetooth

https://store.arduino.cc/index.php?main_page=advanced_search_result&search_in_description=1&keyword=bluetooth&btnG=search

http://blog.miguelgrinberg.com/post/a-cheap-bluetooth-serial-port-for-your-raspberry-pi

https://www.adafruit.com/products/1327

``Bluetooth vs. Wi-Fi (IEEE 802.11)

Bluetooth and Wi-Fi (https://en.wikipedia.org/wiki/Wi-Fi) (the brand name for products using IEEE 802.11 (https://en.wikipedia.org/wiki/IEEE_802.11) standards) have some similar applications: setting up networks, printing, or transferring files. Wi-Fi is intended as a replacement for high speed cabling for general local area network (https://en.wikipedia.org/wiki/Local_area_network) access in work areas. This category of applications is sometimes called wireless local area networks (https://en.wikipedia.org/wiki/Wireless_local_area_network) (WLAN). Bluetooth was intended for portable equipment and its applications. The category of applications is outlined as the wireless personal area network (https://en.wikipedia.org/wiki/Personal_area_network) (WPAN). Bluetooth is a replacement for cabling in a variety of personally carried applications in any setting, and also works for fixed location applications such as smart energy functionality in the home (thermostats, etc.).

Wi-Fi and Bluetooth are to some extent complementary in their applications and usage. Wi-Fi is usually access point-centered, with an asymmetrical client-server connection with all traffic routed through the access point, while Bluetooth is usually symmetrical, between two Bluetooth devices. Bluetooth serves well in simple applications where two devices need to connect with minimal configuration like a button press, as in headsets and remote controls, while Wi-Fi suits better in applications where some degree of client configuration is possible and high speeds are required, especially for network access through an access node.

Wifi

To Wi-fi είναι μια τύπου access point σύνδεση και συνδέεται σε έναν βασικό κόμβο που σου δίνει πρόσβαση στο διαδίκτυο έναντι μιας προσωπικής διεύθυνσης . Έχεις από παντού σύνδεση και πρόσβαση στο βοηθητικό λογισμικό Βασικά μειονεκτήματα είναι πως πρέπει να εισάγεται ο κωδικός πρόσβασης του router και έχει μεγάλη κατανάλωση.

Τα ακριβής χαρακτηριστικά μερικών μοντέλων βρίσκονται παρακάτω :

https://www.arduino.cc/en/Main/ArduinoWiFiShield

https://www.arduino.cc/en/Main/ArduinoBoardYun?from=Products.ArduinoYUN

https://www.sparkfun.com/categories/112

https://www.microchip.com/pagehandler/en-us/technology/wifi/home.html

http://www.digi.com/products/wireless-wired-embedded-solutions/zigbee-rf-modules/point-multipoint-rfmodules/xbee-wi-fi

http://www.st.com/st-web-ui/static/active/en/resource/technical/document/datasheet/DM00102124.pdf

http://www.st.com/st-web-ui/static/active/en/resource/technical/document/datasheet/DM00102124.pdf

http://www.lairdtech.com/product-categories/embedded-wireless/wi-fi-and-wi-fi-bt-modules

https://www.microchip.com/pagehandler/en-us/technology/wifi/home.html

Cellular

Μια λύση είναι η επικοινωνία της συσκευής με την μονάδα επεξεργασίας μέσω ενός φορέα . Δεν είναι απαραίτητο να εφαρμόσουμε την πιο πρόσφατη γενιά , η 2G είναι υπεραρκετή. Αν και ικανοποιούνται πολύ καλά οι περισσότερες από τις προδιαγραφές , έχει βασικό μειονέκτημα την μεγάλη κατανάλωση ισχύος.

Τα ακριβής χαρακτηριστικά μερικών μοντέλων βρίσκονται παρακάτω :

https://www.u-blox.com/en/wireless-modules.html

https://www.arduino.cc/en/Guide/ArduinoGSMShield

http://www.telit.com/products/cellular/overview/

Infrared

IR wireless is the use of wireless (http://searchmobilecomputing.techtarget.com/definition/wireless) technology in devices or systems that convey data through infrared (IR) radiation. Infrared is electromagnetic energy at a wavelength (http://searchnetworking.techtarget.com/definition/wavelength) or wavelengths somewhat longer than those of red light. The shortest-wavelength IR borders visiblered in the electromagnetic radiation spectrum (http://searchcio-midmarket.techtarget.com/definition/electromagnetic-radiation-spectrum);the longest-wavelength IR borders radio waves.

Some engineers consider IR technology to be a sub-specialty of optical technology. The hardware is similar, and the two forms of energy behave in much the same way. But strictly speaking, "optical" refers to visibleelectromagnetic radiation, while "infrared" isinvisible to the unaidedeye. To compound the confusion, IR is sometimes called "infrared light."

IR wireless is used for short- and medium-range communications andcontrol. Some systems operate in line-of-sight mode; this means that theremust be a visually unobstructed straight line through space between the transmitter(source) and receiver (destination). Other systems operate in diffuse mode,also called scatter mode. This type of system can function when the sourceand destination are not directly visible to each other. An example is a televisionremote-control box. The box does not have to be pointed directly at the set,although the box must be in the same room as the set, or just outside the room with thedoor open.

IR wireless technology is used in intrusion detectors; home-entertainment control units; robot control systems; medium-range, line-of-sight laser (http://searchcio-midmarket.techtarget.com/definition/laser) communications; cordless microphones, headsets, modems, and printers and other peripherals.

Unlike radio-frequency (RF) wireless links, IR wireless cannot passthrough walls. Therefore, IR communications or control is generally not possible between different rooms in a house, or between different houses in a neighborhood (unless they have facing windows). This might seem like a disadvantage, but IR wireless is more private than RF wireless. Some IR wireless schemes offer a level of securitycomparable to that of hard-wired systems. It is difficult, for example, toeavesdrop on a well-engineered, line-of-sight, IR laser communications link.

Since the Consumer IR protocols are for the most part not standardized, computers and universal remotes often memorize a bit stream, possibly with compression and possibly without determining the actual bit rate, and play it back. Similarities between remotes are often largely the accidental result of the finite selection of infrared encoder/decoder chips (though now microcontrollers (https://en.wikipedia.org/wiki/Microcontrollers) are also used) and IR receiver modules or imitation of the older chips rather than by design. Manufacturers of consumer appliances often reuse the same protocol on many similar devices, though for each manufacturer and device type there are usually multiple protocols in use. The code listings inform about for any universal remote.

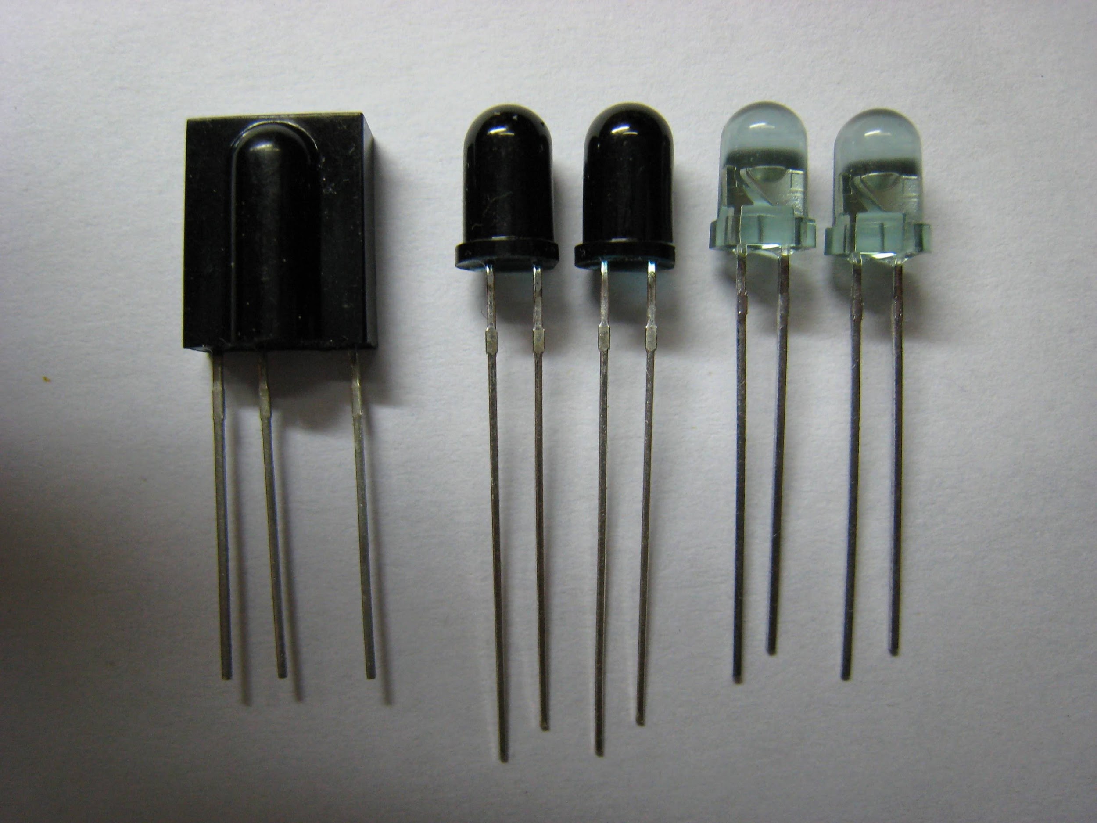
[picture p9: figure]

Δεν υπάρχουν ιδιαιτέρας απαιτήσεις στην προσαρμογή τους στην συσκευή .

Τα ακριβής χαρακτηριστικά μερικών μοντέλων βρίσκονται παρακάτω :

https://learn.sparkfun.com/tutorials/ir-communication

https://www.modmypi.com/blog/raspberry-pis-remotes-ir-receivers

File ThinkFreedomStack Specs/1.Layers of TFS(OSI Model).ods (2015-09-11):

Layer |  | Description | Comments
Output | 8.Actuator | Screen, PC, tablet, Home
Information Flow | 7.Output Control | Adaptor for the output of control unit
 | 6.Channel | cable,wifi
Logical synthesis | 5.Control Unit | Microcontroler, Microprocecor, VLSI system
Information Flow | 4.Output Control | Adaptor for the specific Channel
 | 3.Channel | wifi,bluetooth,cable
 | 2.Input Control | Adaptor for the specific stimulus
Input | 1.Stimulus | Sensors,Buttons,Cam,Joystick etc.

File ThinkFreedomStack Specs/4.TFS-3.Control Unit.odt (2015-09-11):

TFS-3.Control Unit

Σε αυτό το επίπεδο θα γίνεται η ουσιαστική αλληλεπίδραση του ατόμου με το επιβοηθητικό λογισμικό , αναλόγως της εισόδου που θα δίνει . Η μονάδα επεξεργασίας θα επεξεργάζεται τα αιτήματα του χρήστη όπως ορίζει το λογισμικό και θα προβάλει το τελικό αποτέλεσμα. Εδώ χρειαζόμαστε κάτι που να είναι μικρο , φτηνό και συμβατό σε κάθε οθόνη (ή και ηχείο) . Ένας προσωπικός υπολογιστής δεν αποτελεί την καλύτερη λύση ακόμα και αν με την πρώτη μάτια φαίνεται η πιο προφανής . Χωρίς να αποκλείουμε το γεγονός ότι μπορεί κάποιος να διαθέτει έναν , θα ψάξουμε εναλλακτικές λύσεις στο εμπόριο που θα μας κάνουν φτηνότερα την ίδια δουλεία Θα πρέπει να είναι ικανό να δέχεται , να επεξεργάζεται και να προβάλει το αποτέλεσμα (οθόνη, ηχείο) .

Δέχεται

Η μονάδα επεξεργασίας θα πρέπει να επικοινωνεί με τους αντίστοιχους τρόπους που επικοινωνεί και το επίπεδο του ερεθίσματος . Επομένως πρέπει να διαθέτει τους δέκτες των USB, bluetooth,ZigBee , υπέρυθρες , Wifi , GSM και να είναι συμβατοί με τους εκπομπούς αυτών. Απαραίτητη συνθήκη είναι να μην διακόπτεται πότε η επικοινωνία με την μονάδα επεξεργασίας ώστε κάθε στιγμή ο ασθενής να μπορεί να ζητήσει βοήθεια. Ίσως μια μόνιμη σύνδεση στο διαδίκτυο να αποτελέσει ένα μεγάλο πλεονέκτημα στις περιπτώσεις που το άτομο είναι αρκετά απομακρυσμένο από την κύρια οθόνη αλληλεπίδρασης Αυτό διότι η μονάδα επεξεργασίας θα μπορέσει να διανείμει μέσω του διαδικτύου σε κάποιο smartphone ή tablet την εικόνα .

Επεξεργάζεται

Η απαίτηση της προβολής γραφικού περιβάλλοντος περιορίζει τις επιλογές και επομένως εδώ χρειάζεται κάτι με κατάλληλες επεξεργαστικές ικανότητες.

Προβάλει

Χωρίς την προβολή των αποτελεσμάτων το άτομό ούτε μπορεί να διαλέξει τι επιθυμεί αλλά ενδεχομένως ούτε και να το εκδηλώσει . Άρα , η μονάδα επεξεργασίας πρέπει να έχει ικανότητα προβολής περιεχομένου

Ενδεικτικές Λύσεις

Πρακτικά οι επιλογές περιορίζοντα σε λύσεις οι οποίες είναι ευρέως διαδεδομένες στο διαδίκτυο μιας και είναι οικονομικές και υπάρχουν πολλές αναφορές σχετικά με τις δυνατότητες εφαρμογής τους εκεί έξω . Τόσο το υλικό όσο και το λογισμικό είναι `ανοιχτά` προς το κοινό επιτρέποντας την πλήρη τροποποίηση τους για κάθε διαφορετική ανάγκη .

Raspberry Pi (II Model B)

Τρέχει ειδική έκδοση Linux γραφικού περιβάλλοντος , 4 USB θήρες και ικανό να δεχτεί πολλούς διαφορετικούς αισθητήρες. Έχει HDMI και audio jack .

(Δέχεται)

Στο raspberry είναι πολύ εύκολο να προσαρτηθεί ένα bluetooth με USB , ένας αισθητήρα υπερύθρων , wifi σε μια από τις USB θύρες , για κάμερα έχει ξεχωριστή θήρα κτλ.

https://www.modmypi.com/blog/raspberry-pis-remotes-ir-receivers

https://www.raspberrypi.org/products/camera-module/

(Επεξεργάζεται)

Το λογισμικό θα πρέπει να γράφει ώστε να τρέχει στο λειτουργικό του Raspberry το οποίο είναι βασισμένο σε Linux

(Προβάλει)

Με την έξοδο HDMI και audio jack που διαθέτει είναι πολύ εύκολο να συνδεθεί σε κάθε οθόνη.

pcDuino

http://www.linksprite.com/?page_id=782

The Gizmo

http://www.gizmosphere.org/

Udoo

http://www.udoo.org/

Και ως τελευταία ενδεικτική λύση ,

PC

Θα χρειαστεί μόνο το λογισμικό.

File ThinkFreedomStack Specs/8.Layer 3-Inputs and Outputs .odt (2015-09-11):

Layer 3-Inputs and Outputs

Είσοδος

Έχουμε ορίσει το μήνυμα μας ως μια ακολουθία bit το οποίο περιλαμβάνει κωδικοποιημένα την πληροφορία που θέλουμε να στείλουμε , την συσκευή που χρησιμοποιούμε

Παίρνοντας ως δεδομένο ότι αυτό το μήνυμα εξάγεται από το πρώτο layer κατευθυνόμενο προς την μονάδα επεξεργασίας με επιτυχία , συμφωνούμε πως αυτό θα παραμείνει αυτούσιο .

Ο λόγος της παραπάνω συμφωνίας στηρίζεται στο γεγονός ότι το μήνυμα μας θα περιλαμβάνει τις εξής πληροφορίες κατά αυτήν την σειρά (από δεξιά προς τα αριστερά της ακολουθίας των bit) .

1. Τα πρώτα ( 4 πχ) bit δηλώνουν στην μονάδα επεξεργασίας το είδος της συσκευής αλληλεπίδρασης του που συνδέεται στο πρώτο layer ώστε αυτή να αντιδράσει αναλόγως.
2. τα επόμενα περιέχουν την εντολή που δώσαμε . Συγκεκριμένα :

α) Για κουμπί

1 = πάτημα του κουμπιού

0 = όχιπάτημα κουμπιού

Λίστα με συνδυασμούς πατωμάτων

11 = διπλό κλικ

1 hold = παρατεταμένο κλικ

κτλ

β) Για JoyStick

00 = δεξιά

01 = κάτω

10 = αριστερά

11 = πάνω

γ) (Οποτεδήποτε άλλη συσκευή μπει στην συνέχεια)

….

3) (Τα επόμενα bit θα δηλώνουν άλλες λειτουργίες τις οποίες δεν έχουμε καθορίσει ακόμα

Παράδειγμα κατανόησης 1

Το 1100100101 σημαίνει ….

Έξοδος

(Ιδέα χωρίς ASCII )

Στην έξοδο της μονάδας επεξεργασίας θα έχουμε δυο τύπους .

1. HDMI για απλή προβολή των αποτελεσμάτων σε κάθε μέσο που είναι συμβατό.
2. USB σε περιπτώσεις που συνδεθούμε με υπολογιστή . Το σύστημα μας θα έχει τροποποιηθεί αναλόγως ώστε ο υπολογιστής να το βλέπει ως ποντίκι ή πληκτρολόγιο ή ως οτιδήποτε με την βοήθεια κατάλληλων drivers. Η μονάδα επεξεργασίας θα πρέπει να εκτελεί κατάλληλες βιβλιοθήκες που θα επιτρέπουν να φαίνεται στον υπολογιστή ως μια συσκευή σαν το ποντίκι , για παράδειγμα .

Εύρεση υπάρχοντος λύσεων

1) Raspberry pi 2

2) Άλλα boards τα οποία έχουν μικρότερη κοινότητα στο internet

3)Σχεδίαση κυκλώματος

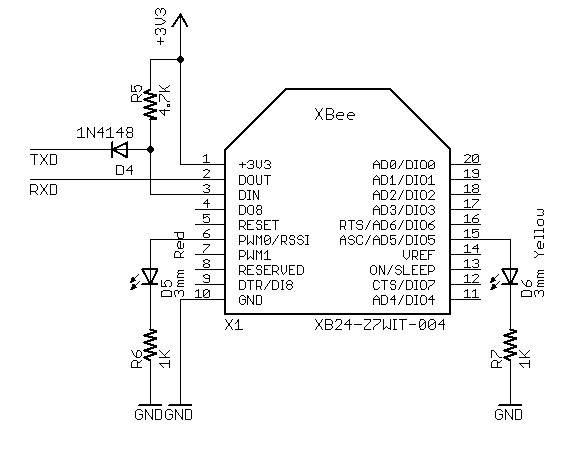
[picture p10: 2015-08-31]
Stuff/Pictures-Schematics/xbee on pi shematic_.png

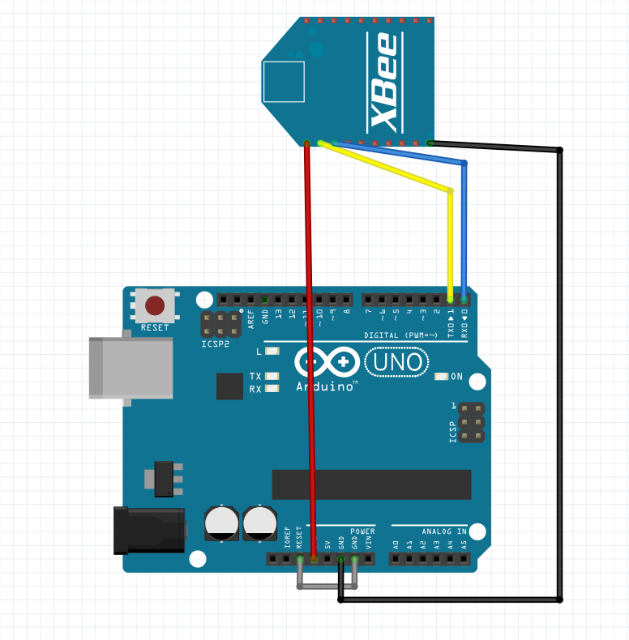
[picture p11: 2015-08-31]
Stuff/Pictures-Schematics/xbee on arduino shematic.png

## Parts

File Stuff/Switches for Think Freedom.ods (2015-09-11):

Type | Name/Manufacter | Price Range | Site | Comments | RoHs complient | the standart that the medical electrical equipment must follow is IEC 60601
Push/Button/Toggle | Peerless Electronics Inc. | 1$-500$ | http://www.peerlesselectronics.com/store/categories/Medical/SWITCHES/?sort=bestselling | It's not categorized by the site. There information about every switch in the description. | see the description of the site | https://en.wikipedia.org/wiki/IEC_60601
Basic Switch | OTTO | around 5$ | http://www.ottoexcellence.com/shop-by-department/basics/ | General use. | yes
Push Botton | OTTO | 1$-4$ | http://www.ottoexcellence.com/shop-by-department/pushbutton/ | Big variety of push bottons from metal to plastic.General use. | yes
Rocker Switch | OTTO | around 5$ | http://www.ottoexcellence.com/shop-by-department/rocker/ | Specific use | yes
Rotary Switch | OTTO | around 5$ | http://www.ottoexcellence.com/products/r2-rotary-switch/ | Specific use. | yes
Slide Switch | OTTO | around 5$ | http://www.ottoexcellence.com/products/slide/ | Specific use | yes
Toggle Switch | OTTO | 3$-4$ | http://www.ottoexcellence.com/shop-by-department/toggle/ | Specific Use | yes
Special Perpuse Switch | OTTO |  | http://www.ottoexcellence.com/products/special-purpose-switches/ | Emergency Push Button,Door interlock switch,FNR. There is a pdf online with a description for every switch | yes
Indicator Light | OTTO | 3$ | http://www.ottoexcellence.com/products/indicator-light/ | General use. | yes
Search window for switches | OMRON |  | https://www.components.omron.com/components/web/webfiles.nsf$FILES/parametric_results.html?ID=2RSET-95L39E&NAME=RESET |  | can see it at every picked switch
Special Disability Access Switches | Technical Solutions Australia | over 80$ | http://tecsol.com.au/cms123/index.php?option=com_content&view=article&id=48&category_id=6&main_cat=6&Itemid=87 | it has big bottons, special shapes. Every switch leads to a mono phono jack. They ship custom plugs and adaptors.
Switch Adaptors/Adaptors in general |  |  | http://www.livingmadeeasy.org.uk/communication/switch-adaptors-for-computer-access-1267-p/
 |  |  | CAMERA
 |  |  | ENTOPISMOS KOUKIDAS(https://www.youtube.com/watch?v=2B6MkqCqG2s)

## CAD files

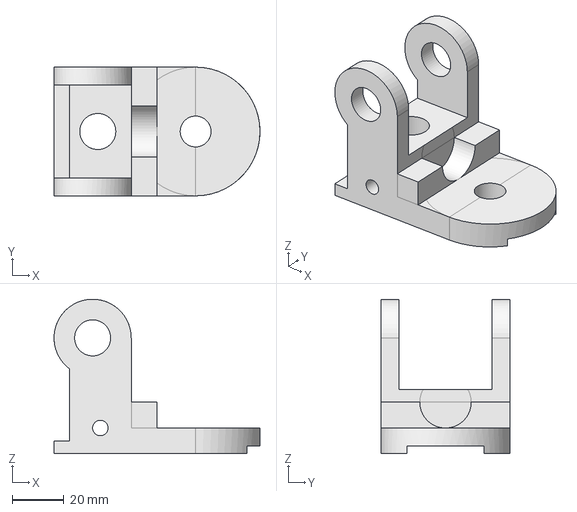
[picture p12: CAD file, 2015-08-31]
Box/fails and more/breaking.fcstd
80.0 x 50.0 x 60.0 mm

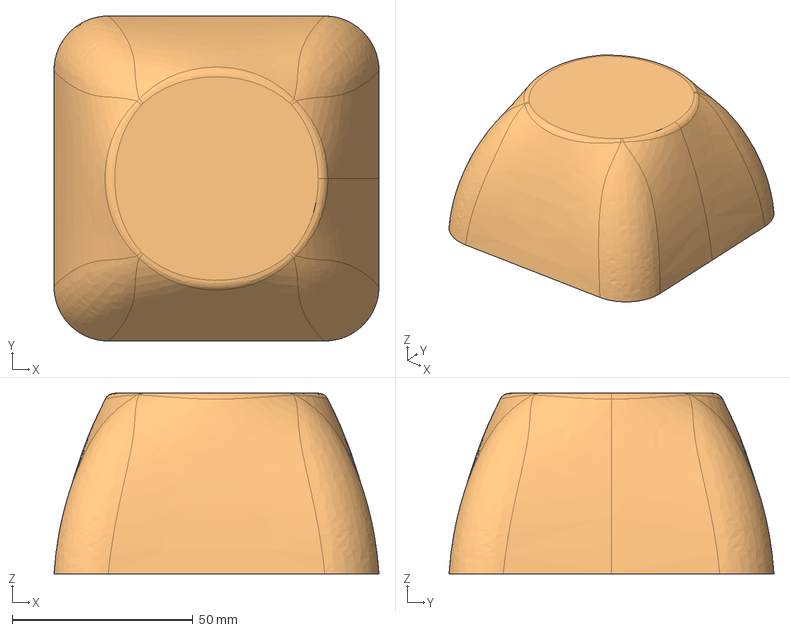
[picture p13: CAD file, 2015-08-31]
Box/v2.fcstd
90.0 x 90.0 x 50.0 mm

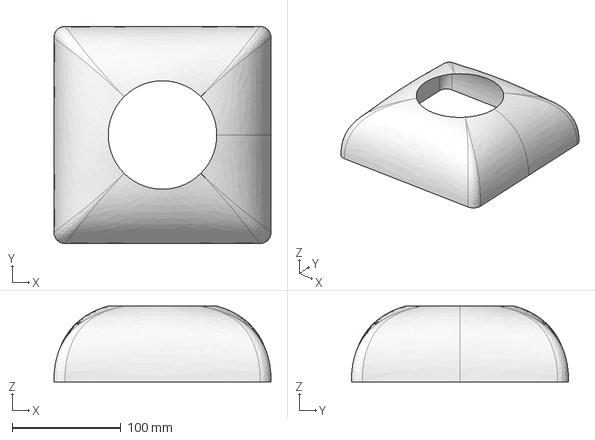
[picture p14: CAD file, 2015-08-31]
Box/fails and more/mark2.fcstd
200.0 x 200.0 x 70.0 mm

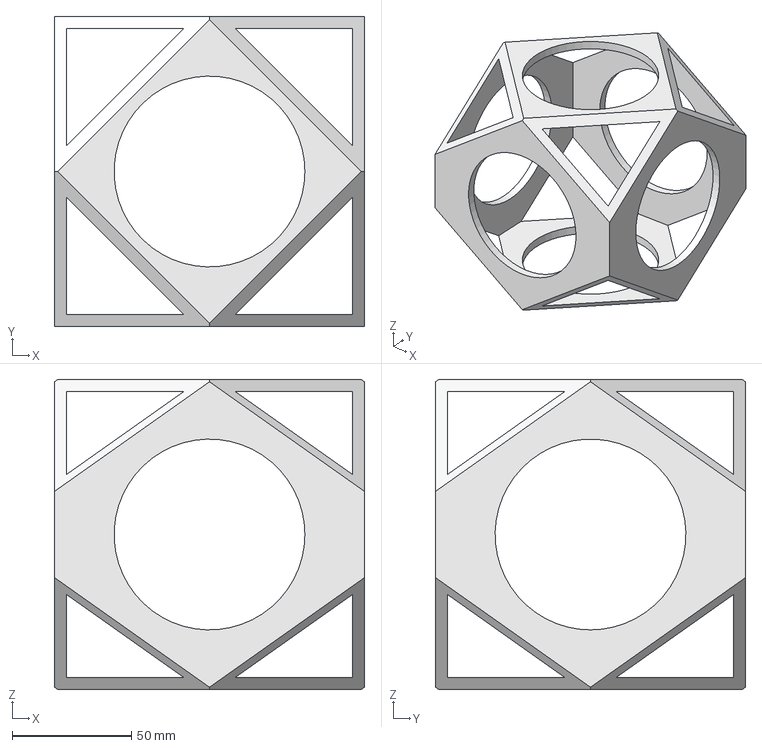
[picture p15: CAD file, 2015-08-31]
Box/fails and more/suoerdupercreationcube.fcstd
130.0 x 130.0 x 130.0 mm

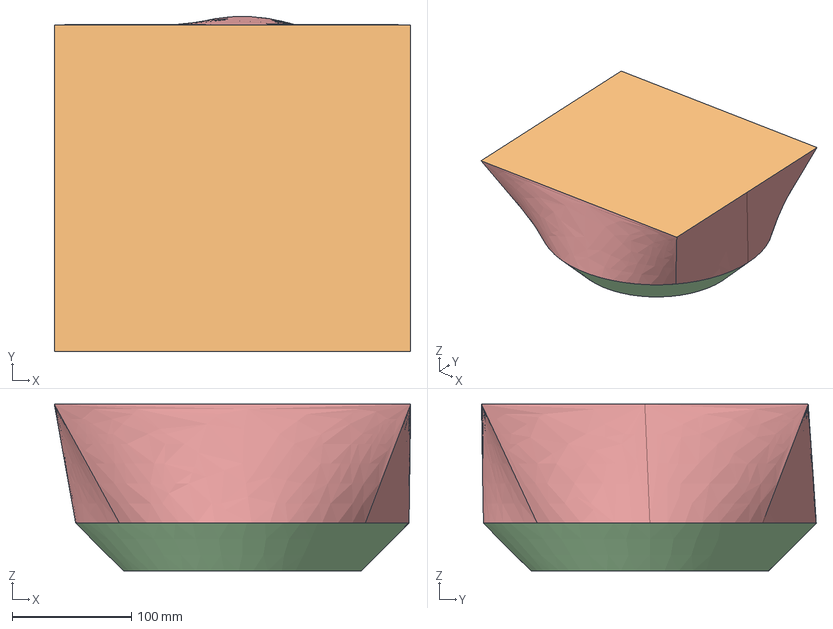
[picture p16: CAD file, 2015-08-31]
Box/fails and more/mark1.fcstd
299.4 x 281.4 x 140.0 mm
Circle
Rectangle
Circle001

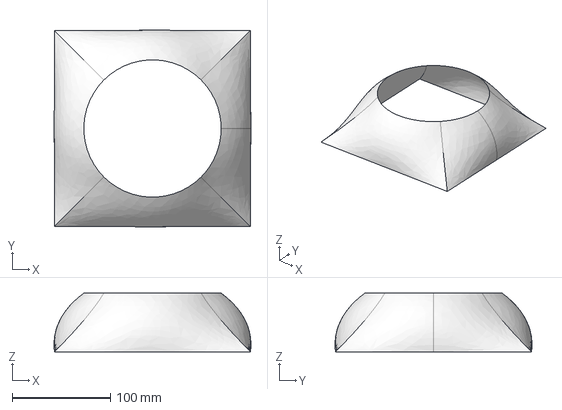
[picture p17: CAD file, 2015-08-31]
Box/fails and more/mark3.fcstd
200.8 x 200.8 x 60.0 mm

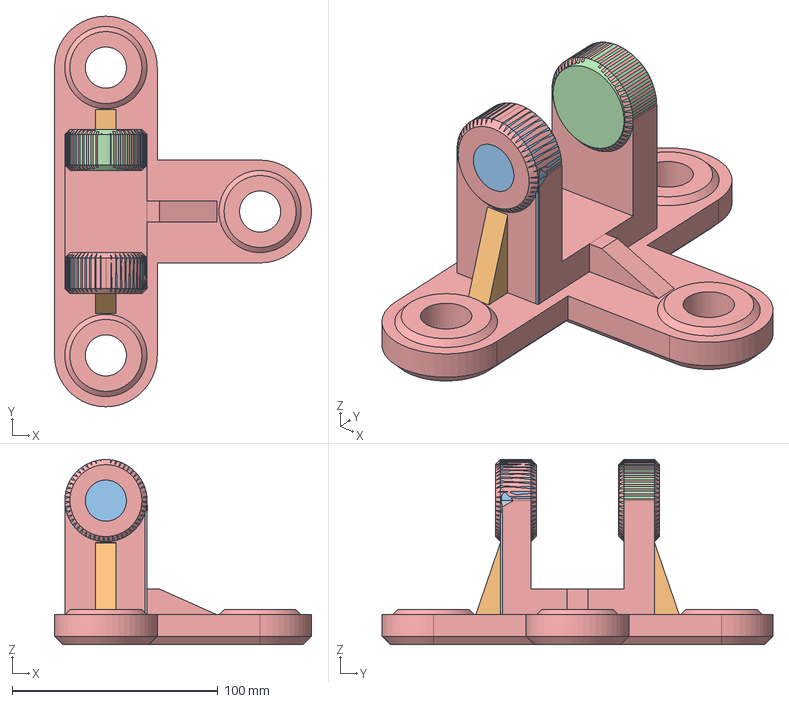
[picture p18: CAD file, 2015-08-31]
Box/fails and more/fork breaking.fcstd
125.0 x 190.0 x 90.0 mm

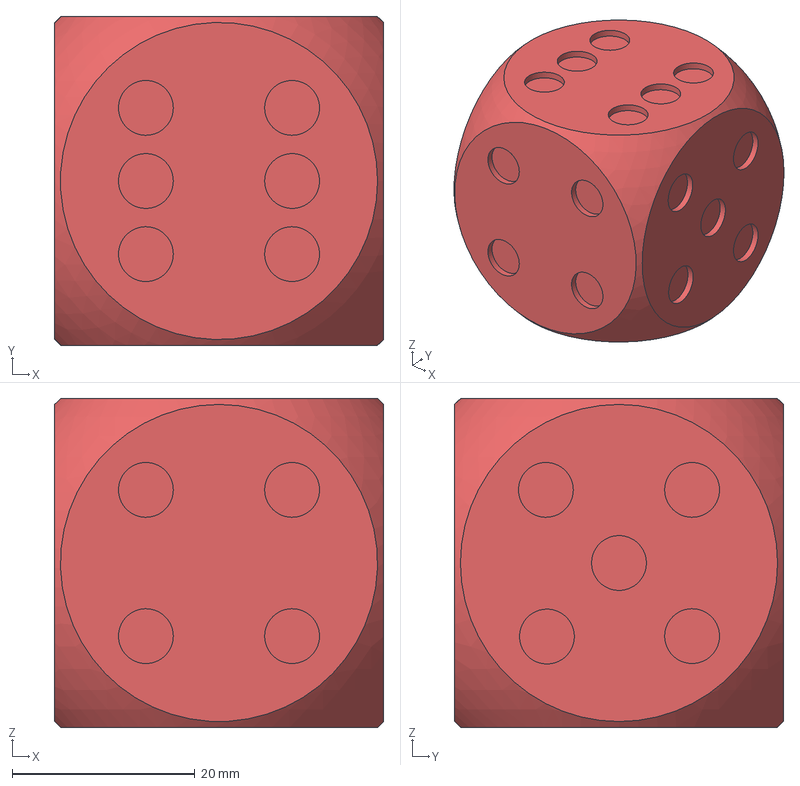
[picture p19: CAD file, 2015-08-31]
Box/fails and more/dise.fcstd
36.0 x 36.0 x 36.0 mm

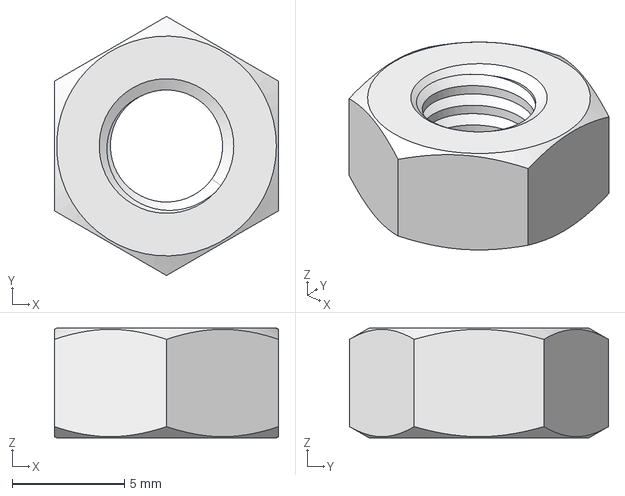
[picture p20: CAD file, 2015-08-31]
Box/fails and more/screwthing.fcstd
10.0 x 11.5 x 4.90 mm

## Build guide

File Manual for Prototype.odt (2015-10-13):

ThinkFreedom Hardware Stack

Manual for the Prototype

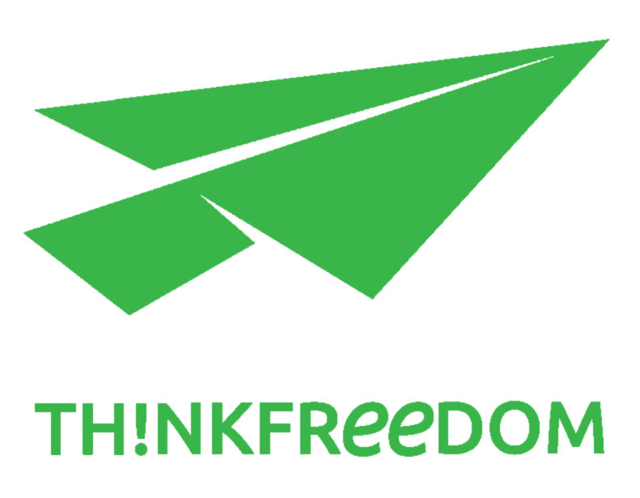
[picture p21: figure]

###### Contents

1. Materials
2. Setting up Xbee
3. Assembling Controller
4. Assembling Control Unit
5. How It Works
6. Further Upgrades

1.Materials

1x Arduino Uno

1x Arduino micro

1x Raspberry Pi (version doesn’t really matter but it would be better to get a Raspberry Pi 2)

1x USB micro for power

1x micro SD card at least 4GB for Pi 2 -or- 1x SD card at least 4GB for Pi 1

1x SD card Adapter for accesing to the SD card or micro SD card

1x HDMI

2x Xbee S1

2x Xbee breakout board

2x Breadboard (you can do it with one but it will be more helpful with two)

2x USB female connector type A

1x USB cable male to male type A

1x USB male A to B (for programming the arduino)

1X Button and 1X 10kΩ resistor (depending on the number of inputs you want. Every input takes one button and one resistor)

1x LED

1X 330 Ohms resistor

Some Jumper wires

Some Pins (male and female)

9x DIP switches , including 2 additional switches on each one. Each DIP switch has 4 pins .Pins 1 and 2 are closer to the OFF state counting from the left to the right and Pins 3 and 4 are in the ON state counting from the left to the right .

And for later if you want to solder everything together :

1x Soldering board

2x Prototyping Box

(Everything can be found on ebay under 10$ (except the Raspberry Pi and the XBees )).

2.Setting up the Xbee

Things we are going to need here:

Software

Arduino IDE (https (https://www.arduino.cc/en/main/software):// (https://www.arduino.cc/en/main/software)www (https://www.arduino.cc/en/main/software). (https://www.arduino.cc/en/main/software)arduino (https://www.arduino.cc/en/main/software). (https://www.arduino.cc/en/main/software)cc (https://www.arduino.cc/en/main/software)/ (https://www.arduino.cc/en/main/software)en (https://www.arduino.cc/en/main/software)/ (https://www.arduino.cc/en/main/software)main (https://www.arduino.cc/en/main/software)/ (https://www.arduino.cc/en/main/software)software (https://www.arduino.cc/en/main/software)). Select the one that matches your OS. This software will be used to program the arduino.

XCTU(http (http://www.digi.com/support/productdetail?pid=3352):// (http://www.digi.com/support/productdetail?pid=3352)www (http://www.digi.com/support/productdetail?pid=3352). (http://www.digi.com/support/productdetail?pid=3352)digi (http://www.digi.com/support/productdetail?pid=3352). (http://www.digi.com/support/productdetail?pid=3352)com (http://www.digi.com/support/productdetail?pid=3352)/ (http://www.digi.com/support/productdetail?pid=3352)support (http://www.digi.com/support/productdetail?pid=3352)/ (http://www.digi.com/support/productdetail?pid=3352)productdetail (http://www.digi.com/support/productdetail?pid=3352)? (http://www.digi.com/support/productdetail?pid=3352)pid (http://www.digi.com/support/productdetail?pid=3352)=3352 (http://www.digi.com/support/productdetail?pid=3352)). Select the one that matches your OS. This software will be used to set up the XBee.

Hardware

Arduino Uno

Jumper Wires

USB Cable A to B

2x Xbee

2x Xbee breakout board

PC

To set up the Xbee we did it through an arduino board. It is more easy if buy a Xbee explorer USB but this way the budget for the project will rise. To set up the Xbee via an Arduino board there are some things to be done.

First, before you connect anything you upload a blank code to the Arduino as appears below. and upload it to the Arduino as USB asp from Tools-->Programmer.

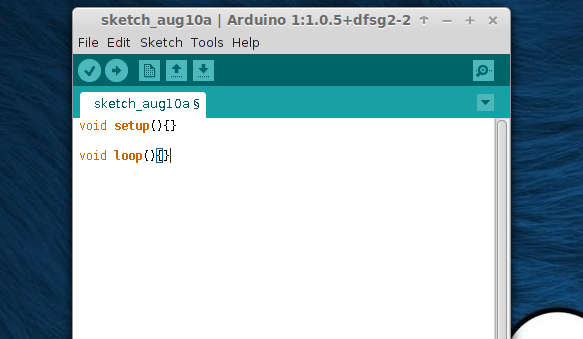
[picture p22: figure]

Next connect the pin as appears below:

Xbee Arduino

+3.3v 3.3V

GND GND

TX TX

RX RX

Also you can connect the reset and GRD of the Arduino or remove the ATmega chip. This way you can bypass the chip and set up the Xbee. This step is optional ,as the blank code you uploaded does the same thing.

The schematics for the connections is:


Next you connect the Arduino to the PC and open the XCTU software.

When you open the software. At the top left corner select the “Add a radio module specifying the port settings”.

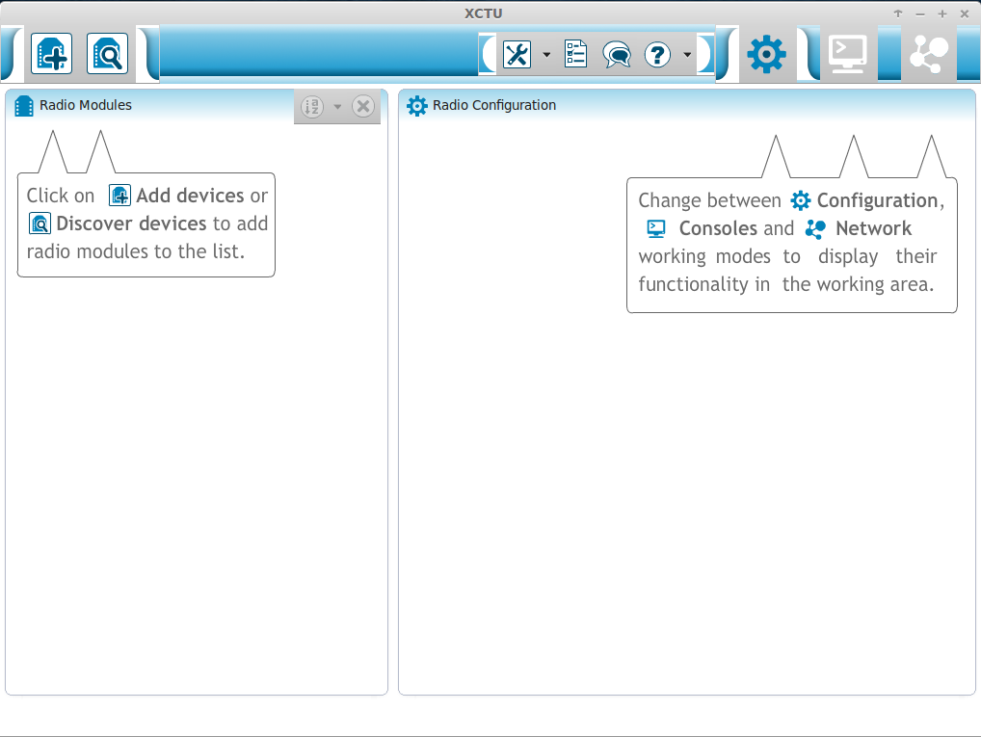
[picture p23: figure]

From the window that will pop select “Provide a port name manually” and put the serial port that the Arduino is connected. For me is /ttyACM0 because i was using Linux. To find in Linux the serial port that the Arduino is connected type in terminal “dmesg | grep tty” (without the “ ”). To find the serial port in Windows go to Device Manager and see what COM port your Arduino is connected. For Mac OS it should be something like this “/dev/cu.usbmodemfd131 or 141 “ but look at here for more information on how to find the right name of the USB : https (https://support.apple.com/en-us/HT202875):// (https://support.apple.com/en-us/HT202875)support (https://support.apple.com/en-us/HT202875). (https://support.apple.com/en-us/HT202875)apple (https://support.apple.com/en-us/HT202875). (https://support.apple.com/en-us/HT202875)com (https://support.apple.com/en-us/HT202875)/ (https://support.apple.com/en-us/HT202875)en (https://support.apple.com/en-us/HT202875)- (https://support.apple.com/en-us/HT202875)us (https://support.apple.com/en-us/HT202875)/ (https://support.apple.com/en-us/HT202875)HT (https://support.apple.com/en-us/HT202875)202875 (https://support.apple.com/en-us/HT202875) . You can also try the auto detection option of your Xbee .

Fill the gaps as appears below. The serial port that you have, Baud Rate at 9600, Data Bits at 8, Parity at None, Stop Bits 1, Flow Control at None. And then click finish.

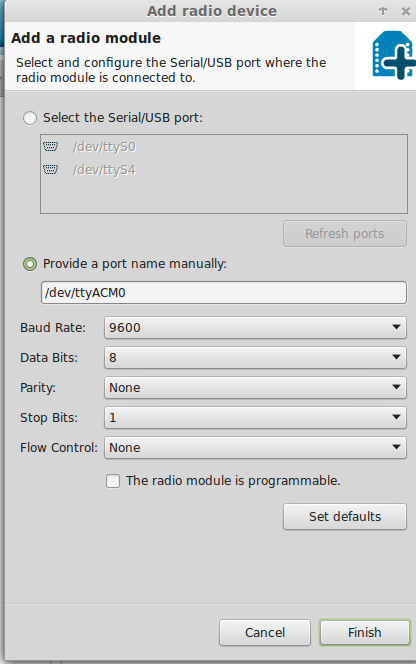
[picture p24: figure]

The next window should pop up:

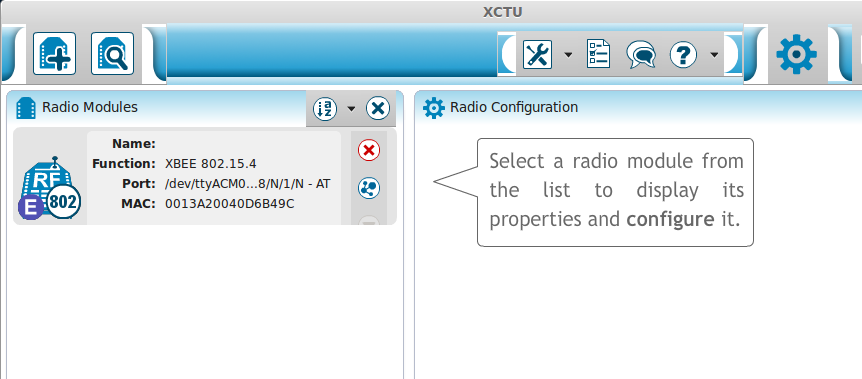
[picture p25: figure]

Select the Xbee that it found. The default setup should start on it’s own.

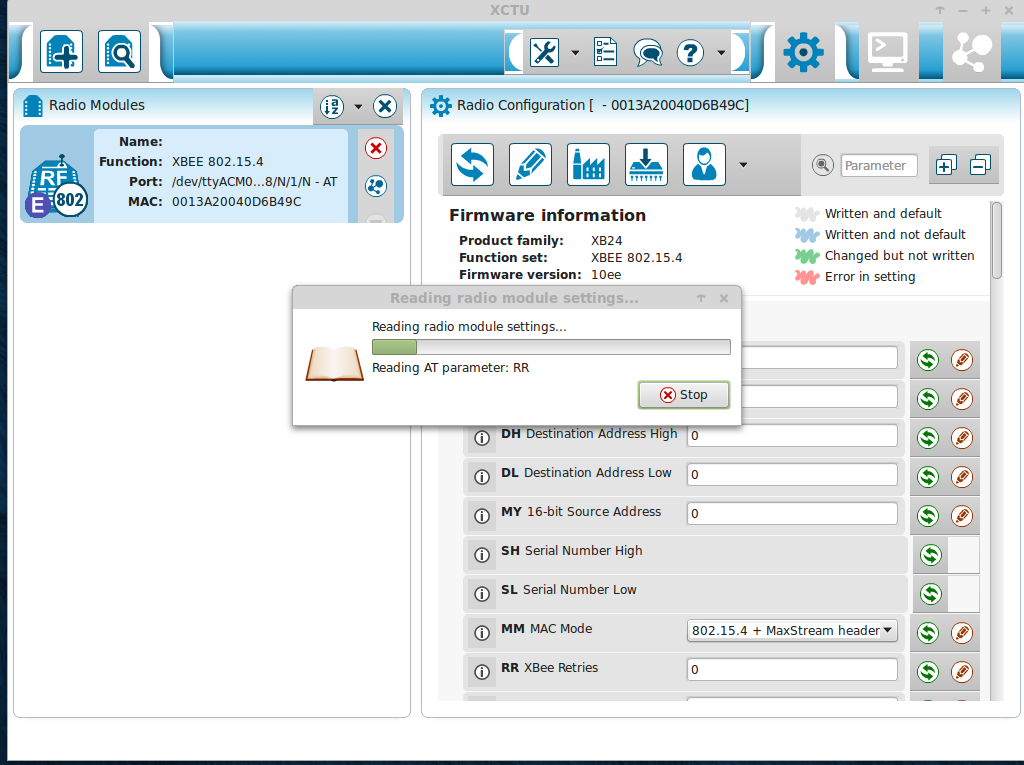
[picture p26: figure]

This set up we are gonna need for this project. Because the connection we want is peer to peer, the default setup does exactly that. The only thing you will to pay attention is that the channel CH and the PAN ID ID for both setups must be the same.

For me the Channel CH is C and the PAN ID is 3332.

After that the setup is done, you close the window and disconnect the Xbee.

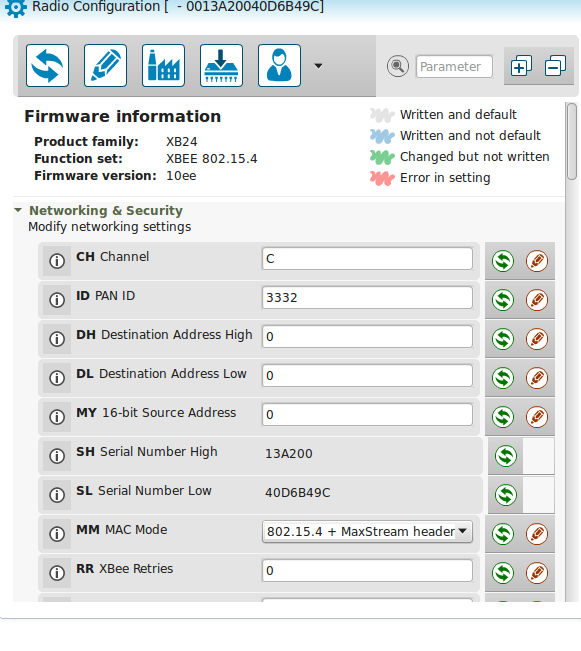
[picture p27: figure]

For the second Xbee you change it and connect it to the Arduino. You follow the same steps to setup it. After that it’s ready to start the wireless communication for your project.

3.Assembling Controller

Things we are going to need here:

Software

Arduino IDE (https (https://www.arduino.cc/en/main/software):// (https://www.arduino.cc/en/main/software)www (https://www.arduino.cc/en/main/software). (https://www.arduino.cc/en/main/software)arduino (https://www.arduino.cc/en/main/software). (https://www.arduino.cc/en/main/software)cc (https://www.arduino.cc/en/main/software)/ (https://www.arduino.cc/en/main/software)en (https://www.arduino.cc/en/main/software)/ (https://www.arduino.cc/en/main/software)main (https://www.arduino.cc/en/main/software)/ (https://www.arduino.cc/en/main/software)software (https://www.arduino.cc/en/main/software)). Select the one that matches your OS. This software will be used to program the arduino.

Code for uploading to the Arduino Uno :

All the codes that will be used are in this link (https://drive.google.com/file/d/0B_OLMcuJEJkcdWVyYXZWQmxiaVU/view?usp=sharing)

(Remember that you can't upload any code to the Arduino when the Tx , Rx pin are connected to the Xbee)

Name of the file : “TFS_input.ino”

const int Button1 = 9;

const int Button2 = 8;

int State2_before;

int State1_before;

void setup(){

pinMode(Button1, INPUT);

pinMode(Button2, INPUT);

Serial.begin(9600);

}

void loop(){

int State1 = digitalRead(Button1);

int State2 = digitalRead(Button2);

if (State2==HIGH && State2_before==LOW){

Serial.println("a");

delay(200);

}

if (State1==HIGH && State1_before==LOW){

Serial.println("a");

delay(200);

}

State2_before=State2;

State1_before=State1;

}

Hardware

1x Arduino Uno

1x Xbee S1

1x Xbee breakout board

1x Breadboard

1x USB female connector type A

1x USB male A to B (for programming the arduino)

1X Button and 1X 10kΩ resistor (depending on the number of inputs you want. Every input takes one button and one resistor)

Some Jumper wires

Some Pins (male and female)

5x DIP switches , including 2 additional switches on each one. Each DIP switch has 4 pins .Pins 1 and 2 are closer to the OFF counting from the left to the right state and Pins 3 and 4 are in the ON state counting from the left to the right

Assembling the Circuit

Xbee :

Solder the Xbee on the breakout board and solder male pins on the outer holes so that the Xbee can connect on the breadboard easily.

Pin 1 = DIP switch 5 to the 1 pin

Pin 2 = DIP switch 4 to the 2 pin + DIP switch 3 to the 2 pin

Pin 3 = DIP switch 4 to the 1 pin + DIP switch 3 to the 1 pin

Pin 10 = DIP switch 5 to the 2 pin

Arduino :

3.3V = DIP switch 5 to the 3 pin

5V = Button pin 1

GND = DIP switch 5 to the 4 pin + 1KΩ resistor pin 2 + Pin 5 of the Arduino

Pin 0 = DIP switch 3 to the 4 pin + DIP switch 4 to the 3 pin

Pin 1 = DIP switch 3 to the 3 pin + DIP switch 4 to the 4 pin

Pin 5 = 1KΩ resistor pin 2 + GND

USB female connector :

VCC = -

D- = DIP switch 1 to the 4 pin

D+ = DIP switch 2 to the 3 pin

GND = DIP switch 1 to the 3 pin

DIP switch 1 :

Pin 1 = GND

Pin 2 = DIP switch 3 www.hobbytronics.co.uk/raspberryto the 1 pin + DIP switch 4 to the 1 pin

Pin 3 = GND of the USB female connector

Pin 4 = D- of the USB female connector

DIP switch 2 :

Pin 1 = DIP switch 3 to the 2 pin + DIP switch 4 to the 2 pin

Pin 2 = -

Pin 3 = D+ of the USB female connector

Pin 4 = -

DIP switch 3 :

Pin 1 = DIP switch 1 to the 2 pin + DIP switch 4 to the 1 pin

Pin 2 = DIP switch 2 to the 1 pin + DIP switch 4 to the 2 pin

Pin 3 = Pin 1 of the Arduino + DIP switch 4 to the 4 pin

Pin 4 = Pin 0 of the Arduino + DIP switch 4 to the 3 pin

DIP switch 4 :

Pin 1 = DIP switch 3 to the 1 pin + Pin 3 of Xbee

Pin 2 = DIP switch 3 to the 2 pin + Pin 2 of Xbee

Pin 3 = DIP switch 3 to the 4 pin

Pin 4 = DIP switch 3 to the 3 pin

DIP switch 5 :

Pin 1 = Pin 1 of the Xbee

Pin 2 = Pin 10 of the Xbee

Pin 3 = 3.3V of the Arduino

Pin 4 = GND of the Arduino

Button :

Pin 1 = 3.3V Arduino

Pin 2 = 330 Ω resistor pin 1

Resistor :

Pin 1 = Pin 2 of the Button

Pin 2 = Pin 5 of the Arduino + GND of the Arduino

It has to look like this :

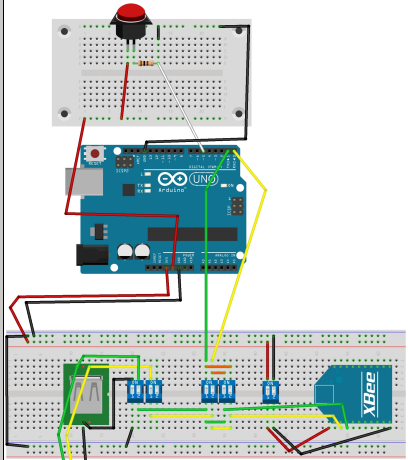
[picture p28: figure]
controller

Uploading Code

(Remember that you can't upload any code to the Arduino when the Tx , Rx pin are connected to the Xbee)

When everything is set you can upload the code to the Arduino via the Arduino IDE program :

Connect the Arduino board to the computer with the USB cable A to B type and wait until the LED s on the board stabilizes .

Compile the the code by clicking the check button on the top left next to the right-pointing-arrow button.

Select the the USB port of the computer which the Arduino is connected from Tools -> Serial Port. For Windows users : the name of the USB port indicates the number of the specific USB port that the Adruino board is connected and in most cases there Arduino has been recognized and his name is written in parentheses next to the name and number of the USB port . For Linux users : the name of the USB port in which the Arduino board is connected looks like this : “ /dev/ttyAMC0 “ or “/dev/ttyAMC1” .For MAC see here how to connect the Arduino : https (https://www.arduino.cc/en/Guide/MacOSX):// (https://www.arduino.cc/en/Guide/MacOSX)www (https://www.arduino.cc/en/Guide/MacOSX). (https://www.arduino.cc/en/Guide/MacOSX)arduino (https://www.arduino.cc/en/Guide/MacOSX). (https://www.arduino.cc/en/Guide/MacOSX)cc (https://www.arduino.cc/en/Guide/MacOSX)/ (https://www.arduino.cc/en/Guide/MacOSX)en (https://www.arduino.cc/en/Guide/MacOSX)/ (https://www.arduino.cc/en/Guide/MacOSX)Guide (https://www.arduino.cc/en/Guide/MacOSX)/ (https://www.arduino.cc/en/Guide/MacOSX)MacOSX (https://www.arduino.cc/en/Guide/MacOSX)

Select Tools -> Programmer -> AVRISP mkll

Finally make sure the your model of the Arduino board is selected (Uno) from Tools -> Board -> Arduino Uno

Switch OFF both switches of DIP switch 3 .

Upload the code clicking on the right-pointing-arrow button in the top left.

Switch ON both switches of DIP switch 3 .

4.Assembling Control Unit

Software

Raspberry

1. At first we need to put an image in the Raspberry Pi. We used the Raspbian, you can find the image and download it here (https://www.raspberrypi.org/downloads/raspbian/) : (https (https://www.raspberrypi.org/downloads/raspbian/):// (https://www.raspberrypi.org/downloads/raspbian/)www (https://www.raspberrypi.org/downloads/raspbian/). (https://www.raspberrypi.org/downloads/raspbian/)raspberrypi (https://www.raspberrypi.org/downloads/raspbian/). (https://www.raspberrypi.org/downloads/raspbian/)org (https://www.raspberrypi.org/downloads/raspbian/)/ (https://www.raspberrypi.org/downloads/raspbian/)downloads (https://www.raspberrypi.org/downloads/raspbian/)/ (https://www.raspberrypi.org/downloads/raspbian/)raspbian (https://www.raspberrypi.org/downloads/raspbian/)/ (https://www.raspberrypi.org/downloads/raspbian/)).

There is a good installation guide of how you are going to put in the Micro SD card. The link (https://www.raspberrypi.org/documentation/installation/installing-images/README.md) for the guide (https (https://www.raspberrypi.org/documentation/installation/installing-images/README.md):// (https://www.raspberrypi.org/documentation/installation/installing-images/README.md)www (https://www.raspberrypi.org/documentation/installation/installing-images/README.md). (https://www.raspberrypi.org/documentation/installation/installing-images/README.md)raspberrypi (https://www.raspberrypi.org/documentation/installation/installing-images/README.md). (https://www.raspberrypi.org/documentation/installation/installing-images/README.md)org (https://www.raspberrypi.org/documentation/installation/installing-images/README.md)/ (https://www.raspberrypi.org/documentation/installation/installing-images/README.md)documentation (https://www.raspberrypi.org/documentation/installation/installing-images/README.md)/ (https://www.raspberrypi.org/documentation/installation/installing-images/README.md)installation (https://www.raspberrypi.org/documentation/installation/installing-images/README.md)/ (https://www.raspberrypi.org/documentation/installation/installing-images/README.md)installing (https://www.raspberrypi.org/documentation/installation/installing-images/README.md)- (https://www.raspberrypi.org/documentation/installation/installing-images/README.md)images (https://www.raspberrypi.org/documentation/installation/installing-images/README.md)/ (https://www.raspberrypi.org/documentation/installation/installing-images/README.md)README (https://www.raspberrypi.org/documentation/installation/installing-images/README.md). (https://www.raspberrypi.org/documentation/installation/installing-images/README.md)md (https://www.raspberrypi.org/documentation/installation/installing-images/README.md))

2. We need to set the Pi to boot to Desktop Environment. We can do this setting either from the first time we boot it or if skipped it open up a terminal and write:

$ sudo raspi-config

And select to boot directly to Desktop.

3. After that you need to change the keyboard layout of the Raspberry because the “GB” layout is by default. Open up a Terminal and write:

$ sudo dpkg-reconfigure keyboard-layout

Select the US layout. And reboot the Pi to apply the changes.

4. Next step is to enable the Serial Port of the Raspberry Pi, this way we can connect the Xbee and communicate with it. There is a good Guide of how we are going to do that (http (http://www.hobbytronics.co.uk/raspberry-pi-serial-port):// (http://www.hobbytronics.co.uk/raspberry-pi-serial-port)www (http://www.hobbytronics.co.uk/raspberry-pi-serial-port). (http://www.hobbytronics.co.uk/raspberry-pi-serial-port)hobbytronics (http://www.hobbytronics.co.uk/raspberry-pi-serial-port). (http://www.hobbytronics.co.uk/raspberry-pi-serial-port)co (http://www.hobbytronics.co.uk/raspberry-pi-serial-port). (http://www.hobbytronics.co.uk/raspberry-pi-serial-port)uk (http://www.hobbytronics.co.uk/raspberry-pi-serial-port)/ (http://www.hobbytronics.co.uk/raspberry-pi-serial-port)raspberry (http://www.hobbytronics.co.uk/raspberry-pi-serial-port)- (http://www.hobbytronics.co.uk/raspberry-pi-serial-port)pi (http://www.hobbytronics.co.uk/raspberry-pi-serial-port)- (http://www.hobbytronics.co.uk/raspberry-pi-serial-port)serial (http://www.hobbytronics.co.uk/raspberry-pi-serial-port)- (http://www.hobbytronics.co.uk/raspberry-pi-serial-port)port (http://www.hobbytronics.co.uk/raspberry-pi-serial-port))

First,open up a Terminal and write:

$ cd /etc/

$ sudo nano inittab

This file has the command to enable the login prompt and this needs to be disabled. Edit the file and move to the end of the file. You will see a line similar to

T0:23:respawn:/sbin/getty -L ttyAMA0 115200 vt100

Disable it by adding a # character to the beginning. Save the file.

#T0:23:respawn:/sbin/getty -L ttyAMA0 115200 vt100

The next file you need to modify is (open a new Terminal):

$ cd /boot/

$ sudo nano cmdline.txt

The contents of the file look like this dwc_otg.lpm_enable=0 console=ttyAMA0,115200 kgdboc=ttyAMA0,115200 console=tty1 root=/dev/mmcblk0p2 rootfstype=ext4 elevator=deadline rootwait

Remove all references to ttyAMA0 (which is the name of the serial port). The file will now look like this dwc_otg.lpm_enable=0 console=tty1 root=/dev/mmcblk0p2 rootfstype=ext4 elevator=deadline rootwait

Now it’s time to make the python code run:

(https (https://github.com/scify/ThinkFreedomHardware/blob/master/Codes/ControlUnitPython.py):// (https://github.com/scify/ThinkFreedomHardware/blob/master/Codes/ControlUnitPython.py)github (https://github.com/scify/ThinkFreedomHardware/blob/master/Codes/ControlUnitPython.py). (https://github.com/scify/ThinkFreedomHardware/blob/master/Codes/ControlUnitPython.py)com (https://github.com/scify/ThinkFreedomHardware/blob/master/Codes/ControlUnitPython.py)/ (https://github.com/scify/ThinkFreedomHardware/blob/master/Codes/ControlUnitPython.py)scify (https://github.com/scify/ThinkFreedomHardware/blob/master/Codes/ControlUnitPython.py)/ (https://github.com/scify/ThinkFreedomHardware/blob/master/Codes/ControlUnitPython.py)ThinkFreedomHardware (https://github.com/scify/ThinkFreedomHardware/blob/master/Codes/ControlUnitPython.py)/ (https://github.com/scify/ThinkFreedomHardware/blob/master/Codes/ControlUnitPython.py)blob (https://github.com/scify/ThinkFreedomHardware/blob/master/Codes/ControlUnitPython.py)/ (https://github.com/scify/ThinkFreedomHardware/blob/master/Codes/ControlUnitPython.py)master (https://github.com/scify/ThinkFreedomHardware/blob/master/Codes/ControlUnitPython.py)/ (https://github.com/scify/ThinkFreedomHardware/blob/master/Codes/ControlUnitPython.py)Codes (https://github.com/scify/ThinkFreedomHardware/blob/master/Codes/ControlUnitPython.py)/ (https://github.com/scify/ThinkFreedomHardware/blob/master/Codes/ControlUnitPython.py)ControlUnitPython (https://github.com/scify/ThinkFreedomHardware/blob/master/Codes/ControlUnitPython.py). (https://github.com/scify/ThinkFreedomHardware/blob/master/Codes/ControlUnitPython.py)py (https://github.com/scify/ThinkFreedomHardware/blob/master/Codes/ControlUnitPython.py))

Warning : This code is only for the case of having the ThinkFreedom Program on PC. This code sends only signals from the Raspberry’s pin to the Micro pins.It doesnt give command on keyboard or mouse of the Raspberry. We need to improve this and change the code to work both for any case.

The code is:

import RPi.GPIO as GPIO

import time

import serial

Button=21

delaytime = 0.03 # psaxnoume gia to grhgorotero on kai off

ser = serial.Serial('/dev/ttyAMA0', 9600)

GPIO.setmode(GPIO.BCM)

GPIO.setwarnings(False)

GPIO.setup(Button, GPIO.OUT, initial=0)

while True:

incoming = ser.readline().strip()

if incoming == 'a':

GPIO.output(Button, 1)

time.sleep(delaytime)

GPIO.output(Button, 0)

print('You pressed : %s' % incoming)

else:

GPIO.output(Button, 0)

print('You pressed Nothing')

GPIO.cleanup()

To run the code open up a Terminal (let’s say you have to your /home/pi folder) and write:

$ cd /home/pi/

$ sudo python ControlUnitPython.py

The code should be running.

6. The last step from the software is to make the python script run on startup at the background.

The guide of how you make this happen is this (http://www.raspberrypi-spy.co.uk/2014/05/how-to-autostart-apps-in-rasbian-lxde-desktop/). (http (http://www.raspberrypi-spy.co.uk/2014/05/how-to-autostart-apps-in-rasbian-lxde-desktop/):// (http://www.raspberrypi-spy.co.uk/2014/05/how-to-autostart-apps-in-rasbian-lxde-desktop/)www (http://www.raspberrypi-spy.co.uk/2014/05/how-to-autostart-apps-in-rasbian-lxde-desktop/). (http://www.raspberrypi-spy.co.uk/2014/05/how-to-autostart-apps-in-rasbian-lxde-desktop/)raspberrypi (http://www.raspberrypi-spy.co.uk/2014/05/how-to-autostart-apps-in-rasbian-lxde-desktop/)- (http://www.raspberrypi-spy.co.uk/2014/05/how-to-autostart-apps-in-rasbian-lxde-desktop/)spy (http://www.raspberrypi-spy.co.uk/2014/05/how-to-autostart-apps-in-rasbian-lxde-desktop/). (http://www.raspberrypi-spy.co.uk/2014/05/how-to-autostart-apps-in-rasbian-lxde-desktop/)co (http://www.raspberrypi-spy.co.uk/2014/05/how-to-autostart-apps-in-rasbian-lxde-desktop/). (http://www.raspberrypi-spy.co.uk/2014/05/how-to-autostart-apps-in-rasbian-lxde-desktop/)uk (http://www.raspberrypi-spy.co.uk/2014/05/how-to-autostart-apps-in-rasbian-lxde-desktop/)/2014/05/ (http://www.raspberrypi-spy.co.uk/2014/05/how-to-autostart-apps-in-rasbian-lxde-desktop/)how (http://www.raspberrypi-spy.co.uk/2014/05/how-to-autostart-apps-in-rasbian-lxde-desktop/)- (http://www.raspberrypi-spy.co.uk/2014/05/how-to-autostart-apps-in-rasbian-lxde-desktop/)to (http://www.raspberrypi-spy.co.uk/2014/05/how-to-autostart-apps-in-rasbian-lxde-desktop/)- (http://www.raspberrypi-spy.co.uk/2014/05/how-to-autostart-apps-in-rasbian-lxde-desktop/)autostart (http://www.raspberrypi-spy.co.uk/2014/05/how-to-autostart-apps-in-rasbian-lxde-desktop/)- (http://www.raspberrypi-spy.co.uk/2014/05/how-to-autostart-apps-in-rasbian-lxde-desktop/)apps (http://www.raspberrypi-spy.co.uk/2014/05/how-to-autostart-apps-in-rasbian-lxde-desktop/)- (http://www.raspberrypi-spy.co.uk/2014/05/how-to-autostart-apps-in-rasbian-lxde-desktop/)in (http://www.raspberrypi-spy.co.uk/2014/05/how-to-autostart-apps-in-rasbian-lxde-desktop/)- (http://www.raspberrypi-spy.co.uk/2014/05/how-to-autostart-apps-in-rasbian-lxde-desktop/)rasbian (http://www.raspberrypi-spy.co.uk/2014/05/how-to-autostart-apps-in-rasbian-lxde-desktop/)- (http://www.raspberrypi-spy.co.uk/2014/05/how-to-autostart-apps-in-rasbian-lxde-desktop/)lxde (http://www.raspberrypi-spy.co.uk/2014/05/how-to-autostart-apps-in-rasbian-lxde-desktop/)- (http://www.raspberrypi-spy.co.uk/2014/05/how-to-autostart-apps-in-rasbian-lxde-desktop/)desktop (http://www.raspberrypi-spy.co.uk/2014/05/how-to-autostart-apps-in-rasbian-lxde-desktop/)/ (http://www.raspberrypi-spy.co.uk/2014/05/how-to-autostart-apps-in-rasbian-lxde-desktop/))

Save the python script at the pi folder.

Open up a Terminal and write:

$ cd /etc/xdg/lxsession/LXDE-pi

$ sudo nano autostart

At the end add a line by writing:

@sudo python /home/pi/ControlUnitPython.py

Save it and reboot the Pi. The script should be running at the background.

Arduino Micro

Upload this code at the Micro (as mentioned before for the Leonardo ):

https (https://github.com/scify/ThinkFreedomHardware/blob/master/Codes/TFS_Leonardo.ino):// (https://github.com/scify/ThinkFreedomHardware/blob/master/Codes/TFS_Leonardo.ino)github (https://github.com/scify/ThinkFreedomHardware/blob/master/Codes/TFS_Leonardo.ino). (https://github.com/scify/ThinkFreedomHardware/blob/master/Codes/TFS_Leonardo.ino)com (https://github.com/scify/ThinkFreedomHardware/blob/master/Codes/TFS_Leonardo.ino)/ (https://github.com/scify/ThinkFreedomHardware/blob/master/Codes/TFS_Leonardo.ino)scify (https://github.com/scify/ThinkFreedomHardware/blob/master/Codes/TFS_Leonardo.ino)/ (https://github.com/scify/ThinkFreedomHardware/blob/master/Codes/TFS_Leonardo.ino)ThinkFreedomHardware (https://github.com/scify/ThinkFreedomHardware/blob/master/Codes/TFS_Leonardo.ino)/ (https://github.com/scify/ThinkFreedomHardware/blob/master/Codes/TFS_Leonardo.ino)blob (https://github.com/scify/ThinkFreedomHardware/blob/master/Codes/TFS_Leonardo.ino)/ (https://github.com/scify/ThinkFreedomHardware/blob/master/Codes/TFS_Leonardo.ino)master (https://github.com/scify/ThinkFreedomHardware/blob/master/Codes/TFS_Leonardo.ino)/ (https://github.com/scify/ThinkFreedomHardware/blob/master/Codes/TFS_Leonardo.ino)Codes (https://github.com/scify/ThinkFreedomHardware/blob/master/Codes/TFS_Leonardo.ino)/ (https://github.com/scify/ThinkFreedomHardware/blob/master/Codes/TFS_Leonardo.ino)TFS (https://github.com/scify/ThinkFreedomHardware/blob/master/Codes/TFS_Leonardo.ino)_ (https://github.com/scify/ThinkFreedomHardware/blob/master/Codes/TFS_Leonardo.ino)Leonardo (https://github.com/scify/ThinkFreedomHardware/blob/master/Codes/TFS_Leonardo.ino). (https://github.com/scify/ThinkFreedomHardware/blob/master/Codes/TFS_Leonardo.ino)ino (https://github.com/scify/ThinkFreedomHardware/blob/master/Codes/TFS_Leonardo.ino)

const int Button =4;
int State_before;

void setup() {

pinMode(Button, INPUT);
Keyboard.begin();
}

void loop() {
int State = digitalRead(Button);
//if the button is pressed
if(State==HIGH && State_before==LOW){

Keyboard.write('a');
}
State_before=State;
}

Hardware

1x Raspberry Pi (model doesn’t really matter but it would be better to get Raspberry 2)

1x Arduino Micro

1x USB micro for power

1x micro SD card at least 4GB

1x micro SD card at least 4GB for Pi 2 -or- 1x SD card at least 4GB for Pi 1

1x SD card Adapter for accesing into the SD card or micro SD card

1x HDMI

1x Xbee S1

1x Xbee breakout board

1x Breadboard

1x USB female connector type A

1x LED

1X 330 Ohms resistor

Some Jumper wires

Some Pins (male and female)

4x DIP switches , including 2 additional switches on each one. Each DIP switch has 4 pins .Pins 1 and 2 are closer to the OFF state counting from the left to the right and Pins 3 and 4 are in the ON state counting from the left to the right.

Assembling

Xbee :

Solder the Xbee on the breakout board and solder male pins on the outer holes so that the Xbee can connect on the breadboard easily.

Pin 1 = DIP switch 4 to the 1 pin

Pin 2 = DIP switch 3 to the 1 pin + DIP switch 2 to the 1 pin

Pin 3 = DIP switch 3 to the 2 pin + DIP switch 1 to the 2 pin

Pin 10 = DIP switch 4 to the 2 pin

Raspberry Pi :

The following image shows the names of the Raspberry's GPIO pin. The image has the names of the pins which the Raspberry understands originally . This means that if you want to refer to them while programming the Raspberry you will use this coding for the GPIO pins.

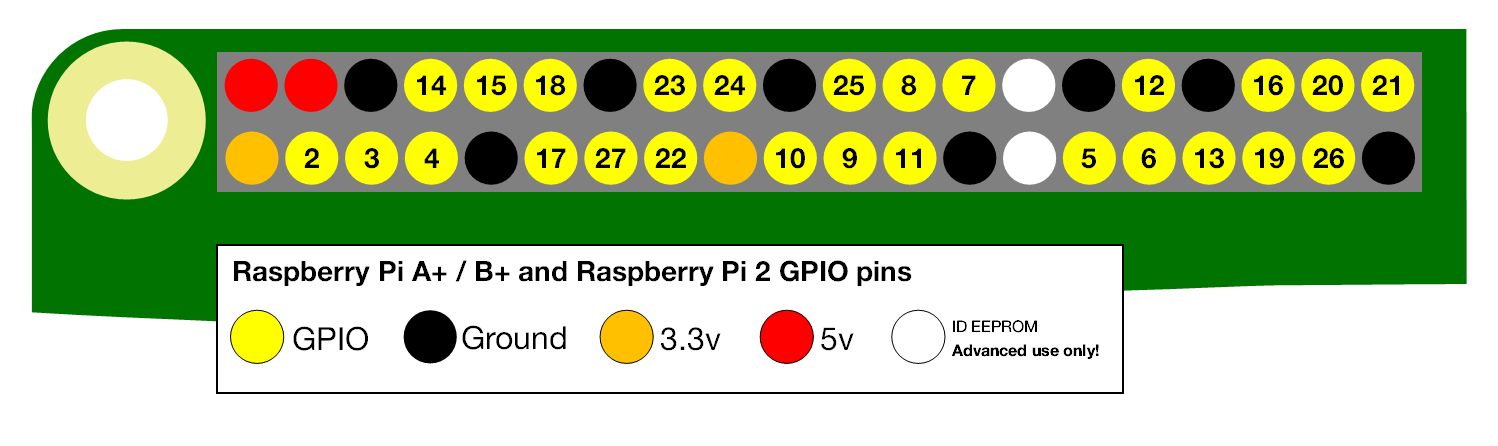
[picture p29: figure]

3.3V = DIP switch 4 to the 3 pin

Ground = DIP switch 4 to the 4 pin + Cathode of the LED +

DIP switch 1 to the 1 pin

Pin 14 (TXD) = DIP switch 3 to the 4 pin

Pin 15 (RXD) = DIP switch 3 to the 3 pin

Arduino Micro :

Pin 4 = Pin 21 of the Raspberry

GND = Ground of Raspberry

USB female connector :

VCC = -

D- = DIP switch 1 to the 4 pin

D+ = DIP switch 2 to the 3 pin

GND = DIP switch 1 to the 3 pin

DIP switch 1 :

Pin 1 = Ground of Raspberry

Pin 2 = DIP switch 3 to the 2 pin + Pin 3 of the Xbee

Pin 3 = GND of the USB female connector

Pin 4 = D- of the USB female connector

DIP switch 2 :

Pin 1 = DIP switch 3 to the 1 pin + Pin 2 of the Xbee

Pin 2 = -

Pin 3 = D+ of the USB female connector

Pin 4 = -

DIP switch 3 :

Pin 1 = DIP switch 2 to the 1 pin + Pin 2 of the Xbee

Pin 2 = DIP switch 1 to the 2 pin + Pin 3 of the Xbee

Pin 3 = Pin 15 (RXD)

Pin 4 = Pin 14 (TXD)

DIP switch 4 :

Pin 1 = Pin 1 of the Xbee

Pin 2 = Pin 10 of the Xbee

Pin 3 = 3.3V of the Raspberry Pi

Pin 4 = Ground of the Raspberry Pi

Resistor :

Pin 1 = Pin 6 of the Xbee

Pin 2 = Anode of the LED

LED :

Anode = Pin 1 of the resistor

Cathode = Ground of the Raspberry Pi

This is the entire prototype assembly :

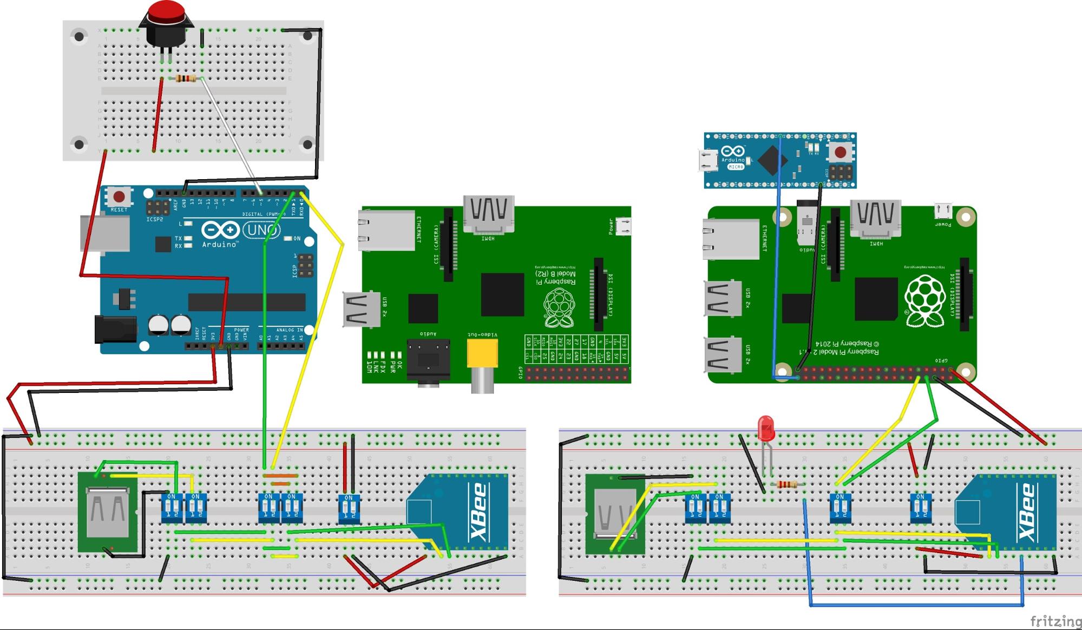
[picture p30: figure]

(This image includes the controller also.At the right is the control unit.The Raspberry Pi 1 in the middle is there only to indicate the TXD and RXD on the pins 14 and 15 which are in the same position on the Pi 2)

Uploading Code

Needs updating:

(APO TA SOFTWARIKA ERGALIA KANOUME TA E3HS GIA NA LEITOURGISEI

Transfer the the codes and the ThinkFreedom program to the Raspberry Pi from the computer with the help of a USB stick.

8a pas ekei kai 8a katebaseis auta to arxeio. 8a pareis auto to arxeio kai 8a to peraseis se ena usb gia na to baleis sto raspberry.

apo auto to link 8a pas kai 8a akolou8hseis tis odhgies “ setting up the development enviroment” wste to raspberry na einai etoimo gia thn egkatastash tou programmatos :

https (https://github.com/scify/JThinkFreedom):// (https://github.com/scify/JThinkFreedom)github (https://github.com/scify/JThinkFreedom). (https://github.com/scify/JThinkFreedom)com (https://github.com/scify/JThinkFreedom)/ (https://github.com/scify/JThinkFreedom)scify (https://github.com/scify/JThinkFreedom)/ (https://github.com/scify/JThinkFreedom)JThinkFreedom (https://github.com/scify/JThinkFreedom) )

5.How it works

After the assembling is complete the system is ready to work . By pressing the button the arduino converts this digital signal into a letter (character or char) . The entirely char is sent from the serial port of the Arduino , with the help of the Xbee or USB cable male to male , to the serial port of the Raspberry . The Raspberry reads this exact letter .Every time it reads a specific letter decides to give a specific command to the ThinkFreedom program to react . Adding different buttons to the system , you have to assign them to different letters and adding different cases when one of them is pressed. The rule of the switches is to alternate from wireless communication to wired and to set up the Xbees without removing them from the assembly . The switches tries to imitate approximately an integrated circuit that does the same work automatically .

Whenever you are running the ThinkFreedom on the PC you are just plug in the Micro of the Control Unit side on a USB port of the PC.

Wireless use :

Turn ON (up) : DIP switches 3 and 5 from the controller side

DIP switches 3 and 4 from the control unit side

Turn OFF (down) : DIP switches 1 , 2 and 4 from the controller side

DIP switches 1 and 2 from the control unit side

Wired use :

Turn ON (up) : DIP switches 1 , 2 and 3 from the controller side

DIP switches 1 , 2 and 3 from the control unit side

Turn OFF (down) : DIP switches 4 and 5 from the controller side

DIP switches 4

Setting up the Xbee from the controller side :

This way is an additional way ( compared to the first one that has been referred before with title “Setting up the Xbee”) of setting up the Xbee from the controller side when you have already assembly all the parts and you do not want to involve with the circuits any more .

Turn OFF (down) : Everything

Upload the blank code to the Arduino following the previous instructions at the “Setting up the Xbee” chapter.

Turn ON (up) : DIP switches 5 and 4 from the controller side

Turn OFF (down) : DIP switches 1 , 2 and 3 .

Run the XCTU program from Digi as it has been already described before in the “Setting up the Xbee” chapter .

(After these steps do not forget to upload the main code to the Arduino (again) )

Setting up the Xbee from the control unit side :

This way is an additional way ( compared to the first one that has been referred before with title “Setting up Xbees”) of setting up the Xbee from the control unit side when you have already assembly all the parts and you do not want to involve with the circuits any more .

From the controller side :

Turn OFF (down) : Everything

From the control unit side :

Turn OFF (down) : Everything

Upload the blank code to the Arduino following the previous instructions at the “Setting up the Xbee” chapter.

From the controller side :

Turn ON (up) : DIP switches 1 , 2 and 3 from the controller side

Turn OFF (down) : DIP switches 4 and 5 from the controller side

From the control unit side :

Turn ON (up) : DIP switches 1 , 2 and 4 from the control unit side

Turn OFF (down) : DIP switches 3 from the control unit side

Run the XCTU program from Digi as it has been already described before in the “Setting up the Xbee “ section .

(After these steps do not forget to upload the main code to the Arduino (again) )

6. Further Upgrades

1.

Logic Circuit that Decides to Switch Between Wireless and Wire Mode :

The DIP switches can be replaced by a specific logic circuit that will do the same job. Considering that the setup procedure will take place independently , before the assembly of the final circuits , the logic circuit could work like this :

The four wires of the USB 2.0 will be used in a different way than the prototype.

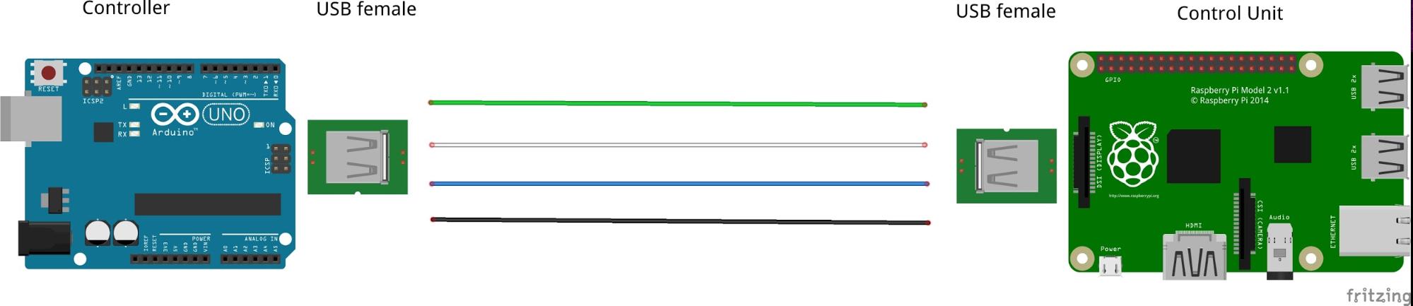
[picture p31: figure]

Green : Tx from the controller (Arduino UNO pin 1)

White : 3.3 V from the control unit side to the controller’s logic circuit as an

input signal that indicates the cable connection.

Blue : 3.3 V from the controller to the control unit’s logic circuit as an input

signal that indicates the cable connection.

Black : Common Ground

(Be careful the Xbee operates only on 3.3 V !)

(Also , be aware that the TXD and RXD in on the one end of the USB are reversing inside the cable to the other end. So the Blue and White cables inside the USB are not as presented at the above image . You have to make another costume reversing of your own ).

From the Controller side the Inputs and Outputs of the logic circuit :

IN : White cable of the usb

1 : when USB is connected.

0 : when USB is disconnected

OUT : Power Supply to the Xbee only on 3.3V
1 : when USB is disconnected.
0 : when USB is connected

From the Control Unit side the Inputs and Outputs of the logic circuit :

IN : Blue cable of the USB

1 : when USB is connected.

0 : when USB is disconnected

OUT : Power Supply to the Xbee only on 3.3V

1 : when USB is disconnected.

0 : when USB is connected

Both logic circuits can be build with one NOT logic gate and one AND logic gate :

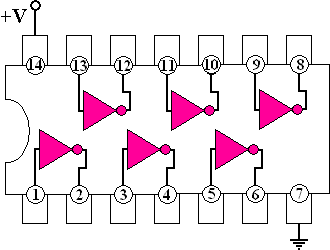
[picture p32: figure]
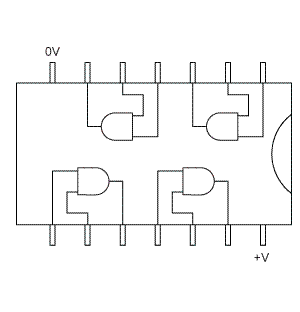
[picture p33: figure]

(The images above show one integrated circuit with 6 NOT logic gates and one integrated circuit with 4 NAND logic gates)

To build the circuits on the controller side :

Make the necessary adjustments to the USB female connector so that you know which cable does what.

Connect the White wire to the Input of the NOT gate .The White wire of the USB cable has 3.3V coming from the Raspberry Pi.

Connect the Output of the NOT gate to the one of the inputs of the AND gate.

Connect the 3.3V of the Arduino to the other input of the same AND gate.

Connect the Output of the AND gate to the 3.3V pin 1 of the Xbee.

Finally , Connect the power supplies of 3.3V and the grounds to the integrated circuits in cause you have got two separate like shown in the image above.

(Remember that you can't upload any code to the Arduino when the Tx , Rx pin are connected to the Xbee)

To build the circuits on the control unit side :

The procedure is similar to the previous.

Done.

Note 1:

To take this upgrade to another level you can use the White Wire coming from the Raspberry Pi at 3.3V to recharge the battery of the controller side.You can do that by spliting the White Wire into two wires when youa re looking the controller side . The one wire can go to the logic circuit as it has been described before . The other one can go to a new circuit that recharges the battery.

Note 2:

All the above have not been tested so in the real world could occur some practical difficulties . In this case you have to reissue the design.

3.

3D Tracking Interface for Input :

http (http://makezine.com/projects/a-touchless-3d-tracking-interface/):// (http://makezine.com/projects/a-touchless-3d-tracking-interface/)makezine (http://makezine.com/projects/a-touchless-3d-tracking-interface/). (http://makezine.com/projects/a-touchless-3d-tracking-interface/)com (http://makezine.com/projects/a-touchless-3d-tracking-interface/)/ (http://makezine.com/projects/a-touchless-3d-tracking-interface/)projects (http://makezine.com/projects/a-touchless-3d-tracking-interface/)/ (http://makezine.com/projects/a-touchless-3d-tracking-interface/)a (http://makezine.com/projects/a-touchless-3d-tracking-interface/)- (http://makezine.com/projects/a-touchless-3d-tracking-interface/)touchless (http://makezine.com/projects/a-touchless-3d-tracking-interface/)-3 (http://makezine.com/projects/a-touchless-3d-tracking-interface/)d (http://makezine.com/projects/a-touchless-3d-tracking-interface/)- (http://makezine.com/projects/a-touchless-3d-tracking-interface/)tracking (http://makezine.com/projects/a-touchless-3d-tracking-interface/)- (http://makezine.com/projects/a-touchless-3d-tracking-interface/)interface (http://makezine.com/projects/a-touchless-3d-tracking-interface/)/ (http://makezine.com/projects/a-touchless-3d-tracking-interface/)

4.

Camera module :

A camera module can be used to detect facial movements . In cases where the abilities of the patient is really limited this is ideal .

Changes in the hardware and software must take place .

It is necessary to easily add the camera without further more adjustments in hardware or software . So the hardware has to change in a way where there will be a female connector for the module “waiting” a plug-in to happen and then automatically adapt to it. The software has to change and have the sensor class of the camera and execute it when it will plug in .

This is the camera module :

https (https://www.raspberrypi.org/help/camera-module-setup/):// (https://www.raspberrypi.org/help/camera-module-setup/)www (https://www.raspberrypi.org/help/camera-module-setup/). (https://www.raspberrypi.org/help/camera-module-setup/)raspberrypi (https://www.raspberrypi.org/help/camera-module-setup/). (https://www.raspberrypi.org/help/camera-module-setup/)org (https://www.raspberrypi.org/help/camera-module-setup/)/ (https://www.raspberrypi.org/help/camera-module-setup/)help (https://www.raspberrypi.org/help/camera-module-setup/)/ (https://www.raspberrypi.org/help/camera-module-setup/)camera (https://www.raspberrypi.org/help/camera-module-setup/)- (https://www.raspberrypi.org/help/camera-module-setup/)module (https://www.raspberrypi.org/help/camera-module-setup/)- (https://www.raspberrypi.org/help/camera-module-setup/)setup (https://www.raspberrypi.org/help/camera-module-setup/)/ (https://www.raspberrypi.org/help/camera-module-setup/)

5.

More Buttons :

In same cases the joystick could be a perfect solution for navigation.

The hardware and software changes are very easy to do.

You have to add more button pins , just like the existing one , on the controller side and then connect them to a USB female connector waiting for a plug in . You have to relate the new buttons with new if cases in the software of the controller side as well as in the control unit side . The ThinkFreedom program should have the flexibility for manual navigation when needed while still having the time lapse navigation.l

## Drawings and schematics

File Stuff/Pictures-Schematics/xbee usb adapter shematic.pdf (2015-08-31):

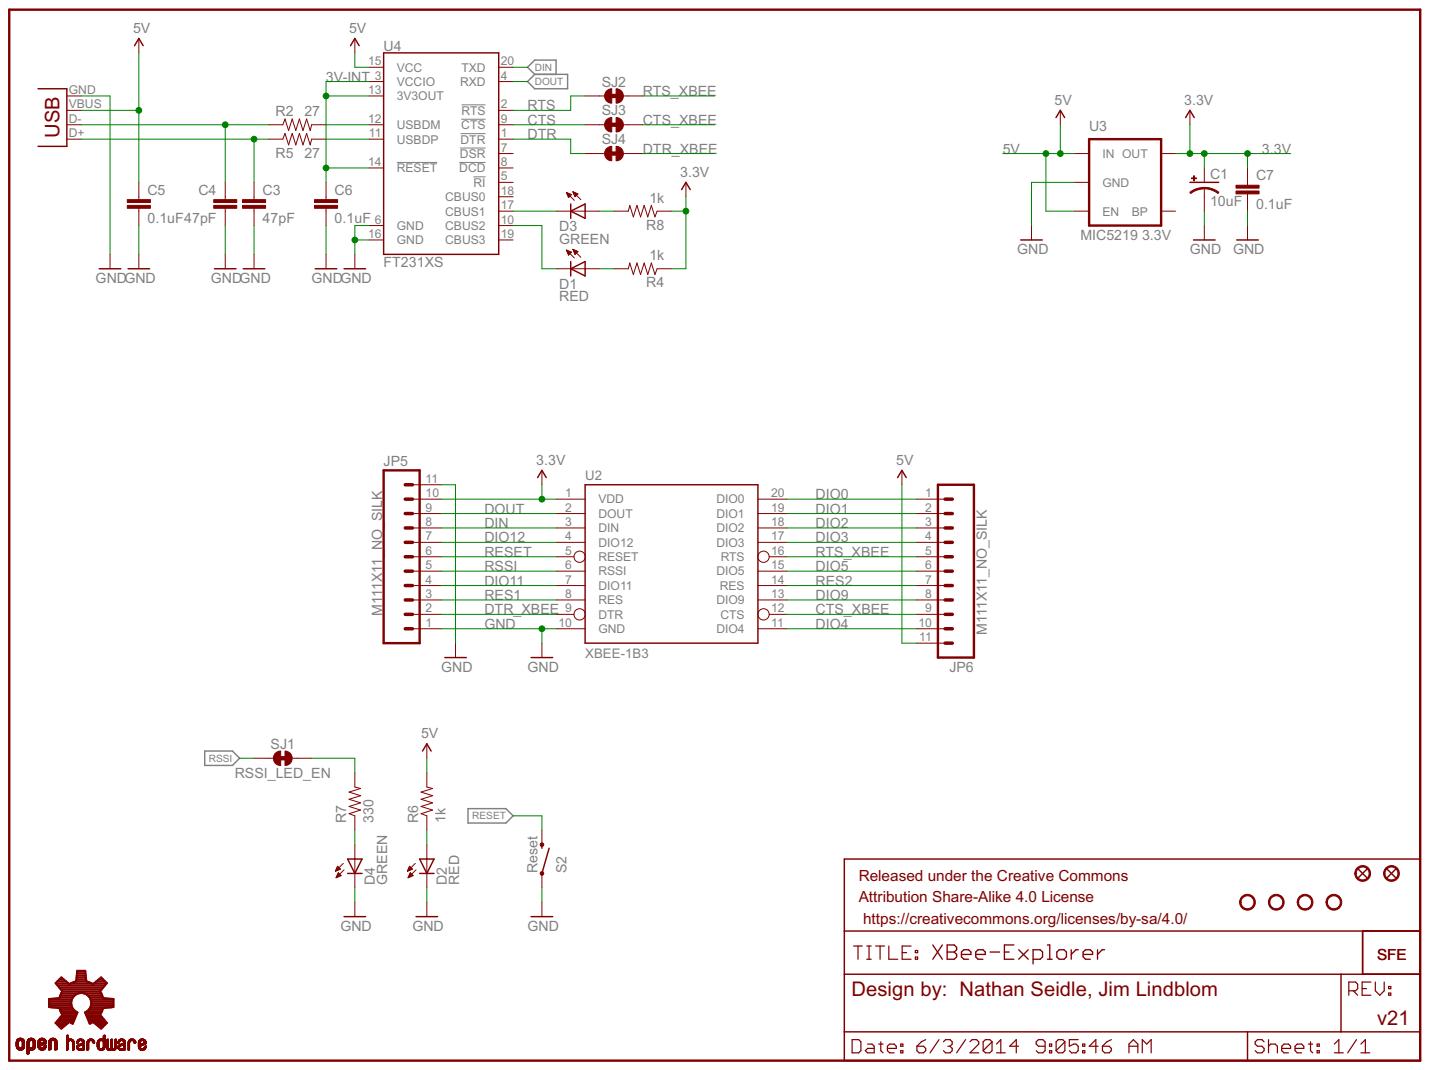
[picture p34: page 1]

19 DIO0 DIO1 | 2
18 DIO1 DIO2 | 3
17 DIO2 DIO3 | 4
16 DIO3 RTS_XBEE 15 RTS DIO5 | 5 6

14 DIO5 | 7
13 RES DIO9 | 8
12 DIO9 CTS_XBEE 11 CTS DIO4 | 9 10

Released under the Creative Commons Attribution Share-Alike 4.0 License

https://creativecommons.org/licenses/by-sa/4.0/

SFE

Design by: Nathan Seidle, Jim Lindblom | v21

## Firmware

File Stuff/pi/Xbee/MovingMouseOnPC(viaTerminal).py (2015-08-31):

import RPi.GPIO as GPIO

up=5
down=6
right=13
left=19
rclick=26
lclick=21
delaytime = 0.03  # psaxnoume gia to grhgorotero on kai off

GPIO.setmode(GPIO.BCM)
GPIO.setwarnings(False)

GPIO.setup(up, GPIO.OUT)
GPIO.setup(down, GPIO.OUT)
GPIO.setup(right, GPIO.OUT)
GPIO.setup(left, GPIO.OUT)
GPIO.setup(rclick, GPIO.OUT)
GPIO.setup(lclick, GPIO.OUT)


while True:
        
    incoming = raw_input('Give a command :  ')
      
    
    if incoming == 'u':
        GPIO.output(up, 1)
        time.sleep(delaytime)
        GPIO.output(up, 0)
        print('You pressed : %s' % incoming)
    elif incoming == 'd':
        GPIO.output(down,1)
        time.sleep(delaytime)
        GPIO.output(down,0)
        print('You pressed : %s' % incoming)
    elif incoming == 'r':
        GPIO.output(right, 1)
        time.sleep(delaytime)
        GPIO.output(right, 0)
        print('You pressed : %s' % incoming)
    elif incoming == 'l':
        GPIO.output(left, 1)
        time.sleep(delaytime)
        GPIO.output(left, 0)
        print('You pressed : %s' % incoming)
    elif incoming == 'b' :
        GPIO.output(rclick, 1)
        time.sleep(delaytime)
        GPIO.output(rclick, 0)
        print('You pressed : %s' % incoming)
    elif incoming == 'a':
        GPIO.output(lclick, 1)
        time.sleep(delaytime)
        print('You pressed : %s' % incoming)
    elif incoming == 'ur':
        GPIO.output(up, 1)
        GPIO.output(right, 1)
        time.sleep(delaytime)
        GPIO.output(up, 0)
        GPIO.output(right, 0)
        print('You pressed : %s' % incoming)
    elif incoming == 'ul':
        GPIO.output(up, 1)
        GPIO.output(left, 1)
        time.sleep(delaytime)
        GPIO.output(up, 0)
        GPIO.output(left, 0)
        print('You pressed : %s' % incoming)
    elif incoming == 'dr':
        GPIO.output(down, 1)
        GPIO.output(right, 1)
        time.sleep(delaytime)
        GPIO.output(down, 0)
        GPIO.output(right, 0)
        print('You pressed : %s' % incoming)
    elif incoming == 'dl':
        GPIO.output(down, 1)
        GPIO.output(left, 1)
        time.sleep(delaytime)
        GPIO.output(down, 0)
        GPIO.output(left, 0)
        print('You pressed : %s' % incoming)
    else:
        GPIO.output(lclick, 0)
        GPIO.output(up, 0)
        GPIO.output(down, 0)
        GPIO.output(right, 0)
        GPIO.output(left, 0)
        GPIO.output(rclick, 0)
        print('You pressed Nothing')        
    
    

GPIO.cleanup()

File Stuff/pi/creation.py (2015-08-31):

import RPi.GPIO as GPIO
import time
import random

GPIO.setmode(GPIO.BCM)
GPIO.setwarnings(False)

LED = 4
right_button = 15
left_button = 14

GPIO.setup(LED, GPIO.OUT)
GPIO.setup(right_button, GPIO.IN, GPIO.PUD_UP)
GPIO.setup(left_button, GPIO.IN, GPIO.PUD_UP)

GPIO.output(LED, 1)

time.sleep(random.uniform(5, 10))

GPIO.output(LED, 0)

while True:
    if GPIO.input(left_button) == False:
            print("Left button pressed")
            break
        if GPIO.input(right_button) == False:
            print("Right button pressed")
            break

GPIO.cleanup()

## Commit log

2015-08-31 Init repo
    [1.Layers of TFS(OSI Model).xlsx, Switches for Think Freedom.xlsx, ThinkFreedomStack Schematic(Fritzing).fzz, Usefull Links.xlsx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]
2015-09-11 Changed files from xlsx->ods.
    [1.Layers of TFS(OSI Model).ods, 1.Layers of TFS(OSI Model).xlsx, Switches for Think Freedom.ods, Switches for Think Freedom.xlsx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]
2015-09-11 Some corrections in tree, removed unwanted stuff.
    [Usefull Links.ods]
2015-10-13 Commiting new files
    [ThinkFreedomStack Schematic(Fritzing).fzz]

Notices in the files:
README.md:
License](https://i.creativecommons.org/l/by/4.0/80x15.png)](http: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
